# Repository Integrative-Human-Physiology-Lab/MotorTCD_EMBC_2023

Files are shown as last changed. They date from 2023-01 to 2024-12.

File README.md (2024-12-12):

# MOTORTCD

The motorTCD project enables the Transcranial doppler probe to be moved with the help of terminal commands. It enables the correct positioning of probe once again even if the signal is lost due to movements or slight jerk.
The project runs on Arduino Uno.

# **GETTING STARTED**
**1. Order the Off-The-Shelf Components:**

  Order the components as listed in the [Bill of Material](https://github.com/Integrative-Human-Physiology-Lab/MotorTCD_EMBC_2023/blob/main/Documentation/BOM.xlsx) for the project.

**2. Print the 3D-printable files:**

Print the STL file as shown in the [Print_Files](https://github.com/Integrative-Human-Physiology-Lab/MotorTCD_EMBC_2023/tree/main/Print_Files).

**3. Start the Assembly:**
The [Assembly Guide](https://github.com/Integrative-Human-Physiology-Lab/MotorTCD_EMBC_2023/blob/main/Documentation/assembly%20guide.pdf) shows you step by step process to assemble and wire the entire project with pictures. The entire assembly process is break down into following steps:
1. Assembly of 3D-printed components
2. Assembly of power components
3. Assembly of motor components
4. Assembly of Arduino with terminal and joystick shield
5. Wiring of all components
6. Final check to ensure connection

This step requires you to have all the components as listed in the Bill of Materials for our project.

**4. Upload the code:**
Connect the Arduino Uno to your computer and upload the Arduino Code.

# **Positioning reference: **

Whenever a signal is locked in. It is always advised that the harness for the TCD probe be placed in the center of the clamp boundaries. Repeated Experimentation has shown that due to the weight of the system, when the subject (individual being experimented on) is made to move in any direction, the TCD probe might be displaced by a very amount in the direction opposite to the moving direction of the subject. As this change in position is very miniscule, putting the probe in the center allows for the position to be adjusted in any direction. 

It is also advised that the person who operates the joystick familiarize themselves with the speed and movement of the clamp for better and more efficient reading.

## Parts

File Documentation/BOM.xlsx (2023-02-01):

Part | Mfct No. | Mfct. | Vendor Part No. | Vendor | Qty. | Unit Price (AUD) | Total | Description | Link
Motor drive controller | L9110S | ??? |  | Makestore.com.au (https://www.makerstore.com.au/product/elec-l9110s-d/) | 2 | $3.20 | $6.40 | DC Motor Drive Module Stepper Motor Drive Controller Board 2.5-12V H-Bridge Can Drive Dual DC Motor at The Same time or 4 Wire 2 Phase Stepper Motor
PLA Roll (White) | Ultimaker PLA | Ultimaker |  | imaginables.com.au (https://imaginables.com.au/collections/filaments/products/ultimaker-pla) | 1 | $76.90 | $76.90 | Ultimaker Material PLA Material White 2.85 mm
Motor | ??? | ??? |  | eBay (https://www.ebay.com/itm/Mini-5mm-2-phase-4-wire-3V-5V-Planetary-Gear-Stepper-Motor-linear-Screw-Slider/191911051181) | 2 | $5.62 | $11.24 | eBay Mini 5mm 2-phase 4-wire 3V 5V Planetary Gear Stepper Motor linear Screw Slider
Arduino Uno R3 | A000066 | ARDUINO CC | A000066 | core-electronics.com.au (https://core-electronics.com.au/arduino-uno-r3.html) | 1 | $35.85 | $35.85 | Controls the Motors
26 AWG, For soldering , Red | 1430-26-1-0500-004-1-TS | CNC Tech | CN472R-25-ND | Digikey (https://www.digikey.com.au/en/products/detail/cnc-tech/1430-26-1-0500-004-1-TS/7063370) | 1 | $11.54 | $11.54 | UL Style 1430 (to solder on motor pads), 26AWG, 4 lead Color Code 1 | Link (https://www.linengineering.com/resources/wiring-diagrams)
26 AWG, For soldering , Green | 1430-26-1-0500-007-1-TS | CNC Tech | CN475G-25-ND | Digikey (https://www.digikey.com.au/en/products/detail/cnc-tech/1430-26-1-0500-007-1-TS/7063373) | 1 | $11.54 | $11.54 | UL Style 1430 (to solder on motor pads), 26AWG, 4 lead Color Code 1 | Link (https://www.linengineering.com/resources/wiring-diagrams)
26 AWG, For soldering, Blue | 1430-26-1-0500-005-1-TS | CNC Tech | CN473L-25-ND | Digikey (https://www.digikey.com.au/en/products/detail/cnc-tech/1430-26-1-0500-005-1-TS/7063371) | 1 | $11.54 | $11.54 | UL Style 1430 (to solder on motor pads), 26AWG, 4 lead Color Code 1 | Link (https://www.linengineering.com/resources/wiring-diagrams)
26 AWG, For soldering, Black | 1430-26-1-0500-001-1-TS | CNC Tech | CN469B-25-ND | Digikey (https://www.digikey.com.au/en/products/detail/cnc-tech/1430-26-1-0500-001-1-TS/7063367) | 1 | $11.54 | $11.54 | UL Style 1430 (to solder on motor pads), 26AWG, 4 lead Color Code 1 | Link (https://www.linengineering.com/resources/wiring-diagrams)
3.3V regulator | AP3429A | Adafruit | ADA4711 | core-electronics.com.au (https://core-electronics.com.au/ap3429a-3-3v-buck-converter-breakout-3-3v-output-1-2a-max.html) | 1 | $7.60 | $7.60 | 3.3V Output 1.2A Max(Buck converter for stable 3V input to the motor)
Switchmode Plugpack(AC to DC Power) | MP-3316 | Core Electronics | CE04425 | core-electronics.com.au (https://core-electronics.com.au/27w-3-12vdc-switchmode-plugpack-with-usb-outlet.html) | 1 | $38.15 | $38.15 | 3V-12VDC 27W power supply(7 output plugs with USB outlet)
Arduino Terminal Block Shield |  | Freetronics | CE04491 | core-electronics.com.au (https://core-electronics.com.au/freetronics-terminal-shield-for-arduino.html) | 1 | $11.95 | $11.95 | Arduino 1.0 / "R3" layout breaks out all 30 pins on current-generation Arduino boards to screw terminals.
Screw kit 1.2-1.6mm |  | HTA | 15875 | hobbytools.com.au (https://www.hobbytools.com.au/Micro-Metric-Screws-600pc) | 1 | $16.48 | $16.48 | M1.6 x 4.5
Sand Paper set |  | Rocket | 1161524 | bunnings.com.au (https://www.bunnings.com.au/rocket-bulk-sanding-sheets-12-piece_p0335354?region_id=117364&gclsrc=aw.ds) | 1 | $8.90 | $8.90 | for roughing out edges during assembly of 3D printed parts
Insert |  |  | INSERTS-420 | serveronthemove.com.au (https://www.serveronthemove.com.au/products/420pc-set-of-knurled-threaded-inserts-m2-m3-m4-and-m5) | 1 | $28.88 | $28.88 | 420pc Set Of Knurled Threaded Inserts (M2, M3, M4 And M5)
Jumper wires for arduino(male,female, both) | ‎EL-CP-004 | ELEGOO |  | amazon.com.au (https://www.amazon.com.au/120pcs-Multicoloured-Dupont-Breadboard-arduino/dp/B01EV70C78?hvadid=341743944651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) | 1 | $9.96 | $9.96 | 120pcs Multicolored Dupont Wire 40pin Male to Female, 40pin Male to Male, 40pin Female to Female Breadboard Jumper Wires
Electrical Tape |  | Viaky | B0744B5DZ2 | amazon.com.au (https://www.amazon.com.au/Electrical-Insulation-Assorted-Colors-Industrial/dp/B0744B5DZ2?s=home-improvement) | 1 | $13.86 | $13.86 | Electrical Insulation Tape
2.1MM DC SOCKET WITH TERMINAL BLOCK | CGTime-00013 | zdyCGTime | B07LFRDSB7 | amazon.com.au (https://www.amazon.com/CGTime-Adapter-terminals-Connector-Security/dp/B07LFRDSB7) | 1 | $10.53 | $10.53 | 5.5 X 2.1mm Female Plug to 2 pin Female Screw terminals adapter

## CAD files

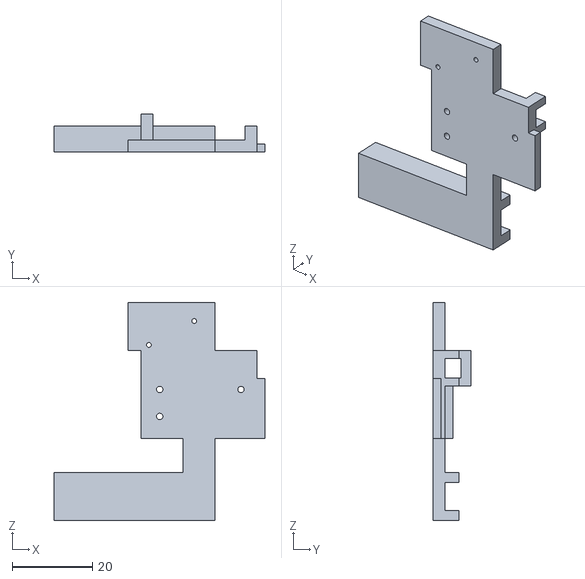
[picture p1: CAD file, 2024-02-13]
Print_Files/Motor Rack B 10_2.STL
52.7 x 9.50 x 54.5

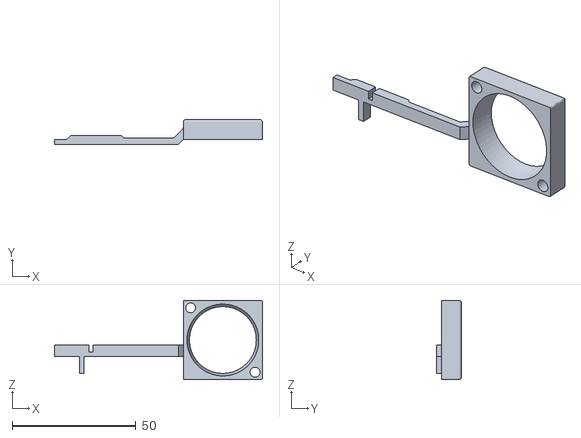
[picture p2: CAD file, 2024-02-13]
Print_Files/Prototype_10_Faceplate 9.STL
84.0 x 10.0 x 32.0

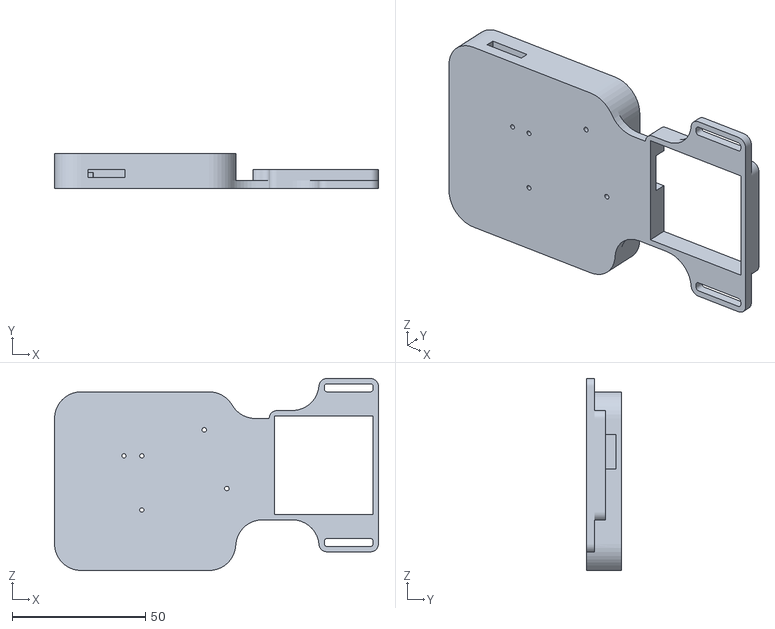
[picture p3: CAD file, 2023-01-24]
Print_Files/Motor Rack A 9.STL
121.5 x 13.0 x 72.0

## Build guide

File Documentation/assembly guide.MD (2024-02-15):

# Motor TCD Assembly Manual

## 1.  3D Printed Components Assembly

1. 	Remove all supports and raft from the print, it is important to ensure that all parts are free from excessive material especially the friction surfaces to ensure smooth movement of the device.

2. 	The motor racks consists of 2 parts - a hollow square at the front to attach to the strap and move the probe around a rectangular box to hold the motor.

3. There are 4 open holes on the rectangular box of motor rack: 1 at the back and 1 on the side for motor wires, 2 at the front to connect the faceplate and innerplate. 

4. With thin bar facing upwards, slide the headplate into through the upper hole on the front face of motor rack

5. Push the headplate as far back into the motor rack as possible 

6.  Tilt the faceplate at an angle where the thin bar is elevated as further away from the surface of motor rack as possible 

7. Align the hollow square of the motor plate with the thin bar of faceplate

8. Slide the inner plate underneath the thin bar at and angle, ensuring that the bar is still align with the hollow square, then, pushes the end of the bar into the square  
*Note: it is important that the small arm of the bar is located in between the closed hollow square and open hollow square)
  (An easier technique is to place the motor plate perpendicular to the end of the thin bar, let the thin bar touches the upper surface then rotate the motor plate slowly underneath the thin bar allowing the end of the bar to go through the hollow square)

9. After the open end of the bar has gone through the closed hollow square, push the 
inner plate forward the front face while also applying downward pressure so the motor 
plate lays flat onto the motor rack 

10. A 'click' sound should be hear when the motor plate snaps into place 

11. Ensure that all the movement are smooth (up and down movement along the motor plate of the faceplate and side movement of motor plate inside the motor rack)

12. If the movement is not smooth, remove the parts and smoothen all friction surface 
then repeat from step 4 

13. If all movements are smooth, close the lid of motor rack to complete the assembly 
(move rotation may be needed to put the lid into place)

## 2. Power Components Assembly

-Parts Needed: 
1. SwitchMode Plugpack(1) 
2. 2.1MM DC SOCKET WITH TERMINAL BLOCK (1) 
3. 22 AWG Wires: red and green (1 each 20 cm) 

- **Assembly Steps:** 

1. Turn the power output to 4.5V as the buck converter needs more than 3V for power source.

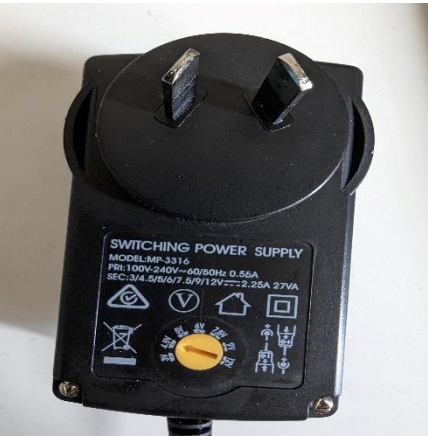
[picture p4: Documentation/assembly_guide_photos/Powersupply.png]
Power supply


2. Take 5.5*2.1 mm jack and plug at the end with matching the arrows. 

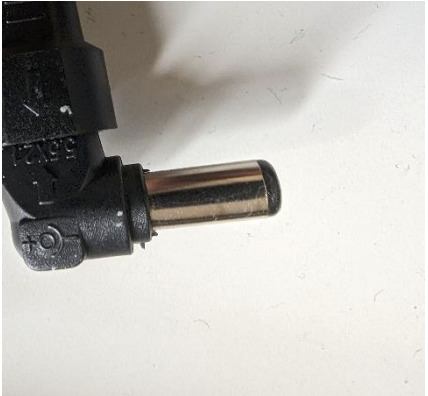
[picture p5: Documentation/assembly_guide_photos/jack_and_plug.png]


3. Wire the 2.1mm DC socket with Terminal Block. Strip the wires. Wire red wire to positive side and green wire to the ground.

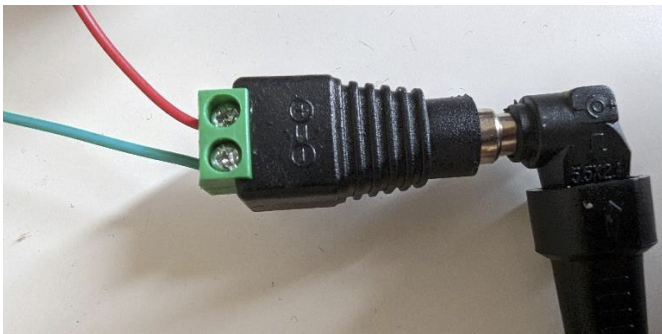
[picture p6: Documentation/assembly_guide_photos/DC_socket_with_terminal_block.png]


## 3. Motor Components Assembly

### a. Stepper Motor Soldering

- **Materials:** 

1. eBay Mini 5mm 2-phase 4-wire 3V 5V Planetary Gear Stepper Motor linear Screw 
Slider-(2 units) 
2. 26 AWG wire for soldering (Yellow, White, Black, Green)- 260 cm length for every 
wire-(2 units)

- **Procedure:**

1. Place the motor horizontally on table and stick the end of the motor flat onto the 
surface where soldering is to be done. 
2. Strip the wires into the length half of the size of the motor soldering plate. 
3. Now solder the wires into this order shown below: 

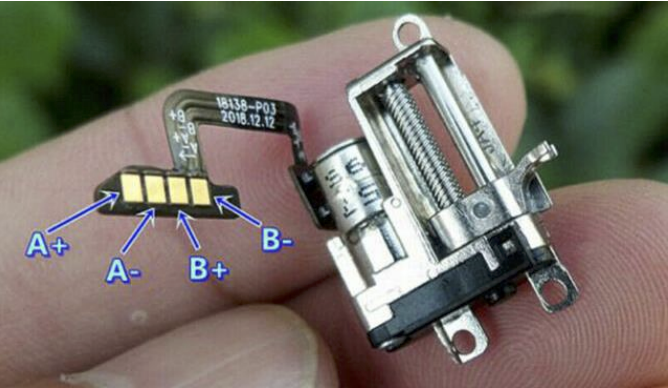
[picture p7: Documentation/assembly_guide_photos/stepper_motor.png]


A+ to yellow wire 

A - to white wire 

B+ to black wire 

B- to green wire

4. The soldering should be done carefully as the pad of motor is very small and two ends can join up during soldering. 
5. The final soldering of the motor look like this: 

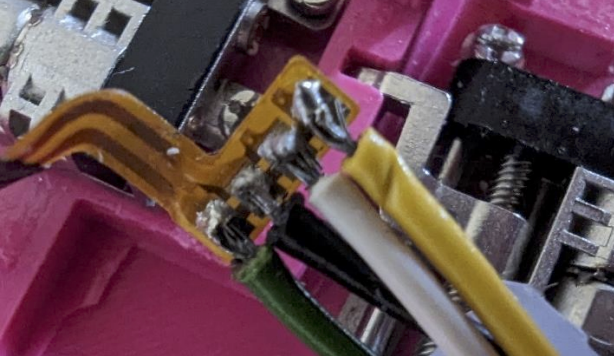
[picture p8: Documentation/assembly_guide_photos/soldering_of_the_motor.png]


6. Similarly, solder the second motor with similar wires in similar order. 

### b. Assembling Motor into 3D Printed Faceplate

- **Materials:** 
1. Soldered two stepper motors 
2. 3D printed Assembly 
3. M1.6*4.5 threaded bolts or screws 

- **Steps:** 
1. Of the two motors, one is responsible for vertical movements and one is 
responsible for horizontal movements. 
2. The vertical movement motor is fixed upon upper three 
holes as shown in figure with its linear actuator fixed in 
the opening to its side. Take three screws and screw the 
three hinges of motor as in figure. 

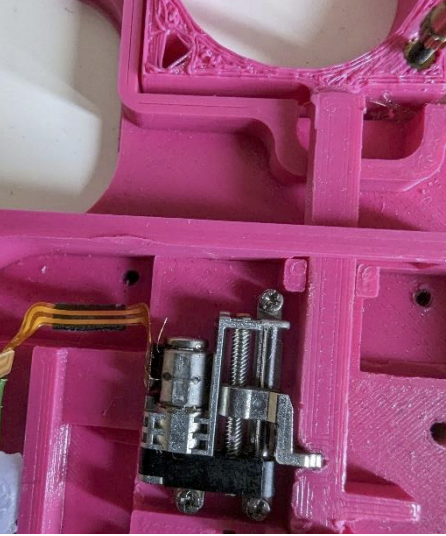
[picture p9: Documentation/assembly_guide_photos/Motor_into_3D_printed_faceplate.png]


3. Similarly, the horizontal movement motor is fixed in 
there holes below the motor with its actuator fixed in 
the opening. 

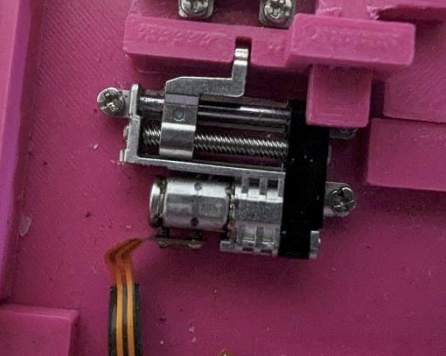
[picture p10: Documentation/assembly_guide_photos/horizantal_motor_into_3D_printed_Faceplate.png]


4. Now take the other end of the wires and line them up in their appropriate way and 
glue them in. There are two holes provided for the end of wires to follow along. 
The final sub-assembly look like this: 

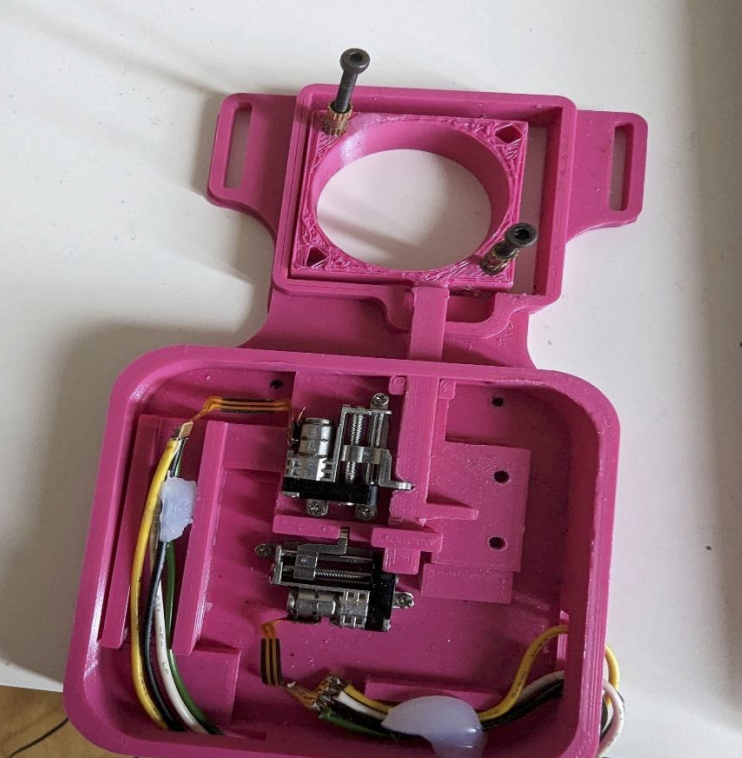
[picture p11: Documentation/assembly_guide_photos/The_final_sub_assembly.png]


### c. Soldering and Wiring 3V Regulator

- **Materials:** 
1. 3V Buck converter set 
2. Some Arduino jumper wires female-female (orange, red and green) 

Steps: 
1. Take the buck converter set and solder the pins into place like 
this. 

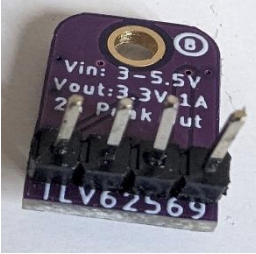
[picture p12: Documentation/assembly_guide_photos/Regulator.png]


2. Now, cut the jumper wires into half and strip the end. 

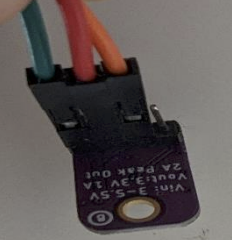
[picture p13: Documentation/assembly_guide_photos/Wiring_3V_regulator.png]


3. Now there are three pins which should be connected to jumper 
wires female like listed below: 
Vin-orange    GND-green   3V-red 

### d. Connecting Stepper Motor Drive Controller

Parts needed: 
1. Sub-assembly obtained from step b 
2. Stepper Motor Drive Controller *2 
3. Arduino female-female jumper wires (2*green, 1*yellow, 1*white, 1*black, 
1*red) *2

Steps: 
1. Strip the loose ends of wire coming from two stepper motor. 
2. Now, these wires (4 each) is connected to the stepper motor drive controller. 
3. Take all 4 wires (yellow, white, black green) from a motor with vertical 
movements and a motor drive controller green end.  
4. The yellow and white wire is wired into Motor A and 
black and green is wired into Motor B. Take reference 
of the picture: 

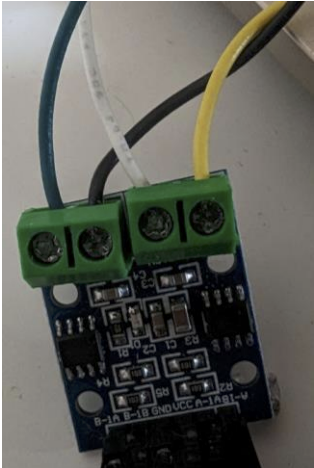
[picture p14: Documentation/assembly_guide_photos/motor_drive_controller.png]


5. Similarly, wire the other motor controller drive with the 
horizontal movement motor. 

6. Now, the opposite end of motor drive controller has 
pins where female Arduino jumper wires should be 
connected. 

7. Cut the Arduino jumper wires into the half and strip the end. 

8. Now connect the female end of jumper wire to the corresponding pin as listed 
below: 

A-1B with yellow 

A-1A with white 

VCC with red 

GND with green 

B-1B with black 

B-1A with green 

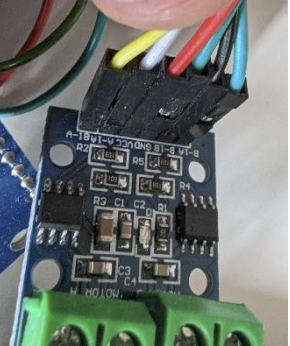
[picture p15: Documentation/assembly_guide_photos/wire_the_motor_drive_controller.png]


9. Similarly, follow the similar steps for another motor and this section is complete. 

## 4. Arduino with Terminal and Joystick Shield Assembly

- **Components:** 
1. Arduino Uno * 1 
2. Terminal Shield *1 
3. Joystick Shield Funduino *1 

Steps: 
1. Take Arduino Uno and on top of that place the terminal shield by aligning the digital and 
analog pins of Arduino with that of terminal shield. 
2. Now take joystick shield and place on top of the black female pins of terminal shield. 
Align the shield accordingly with the number of pins per side. 
3. The sub-assembly is complete. 

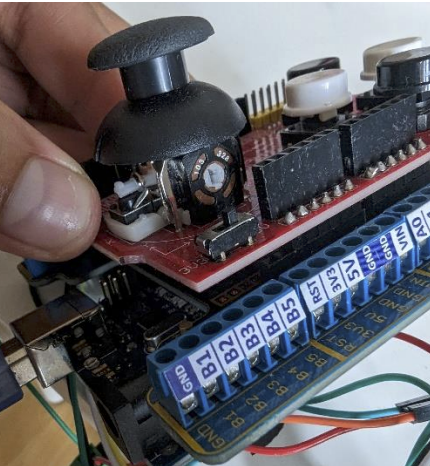
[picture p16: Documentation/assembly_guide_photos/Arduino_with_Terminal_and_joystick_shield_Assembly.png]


## 5. Final Wiring and Check

Parts Needed: 
1. All sub-assemblies created till now. 
2. Green 26 AWG wire of length 20 cm. 

Steps: 
1. Power terminal sub assembly with 3V regulator and Arduino: 
The end of the 2.1MM DC SOCKET WITH TERMINAL BLOCK has two green and 
red loose wires. Strip the end of these wires if needed. Screw the green wire into near 
ground terminal (GND) in Terminal shield. Connect the red wire to the orange wire of 
the 3V regulator. 

2. 3V regulator with motor drive controllers and Arduino. 
Take red wires of the two-motor drive controller (one each) and connect with the red 
wire of 3V regulator. These three wires must be joined together and bonded by an 
electrical tape. 
Now take Green 26 AWG wire of length 20 cm and strip both ends. Take green wires 
(GND not B-1A) of the two motor drive controller (one each) and connect with the 
green wire of 3V regulator and the one end of the Green 26 AWG wire of length 20 
cm. These four wires must be joined together and bonded by an electrical tape. Now 
take the free end of Green 26 AWG wire of length 20 cm and connect to the near 
ground terminal (GND) in Terminal shield. 

3. Motor drive controller with Arduino 
Now there are four wires (yellow, white, black and green) left in motor drive controller 
which should be connected to the respective pins in Arduino.  

|Vertical Movement Motor | Horizontal Movement Motor| 
|----------- | ----------- |
| Yellow(A2) | Yellow(D9) |
| White(A3) | White(D10) |
|Black(A4)  | Black(D11) |
|Green(A5)  |Green(D12) |
 
Connect these wires into Terminal shield and screw it accordingly. 

5. Final Check 

• Connect the power supply and both red LED from motor controller drivers should 
turn on. If not, check your connect again from Step 2 and check the wiring as grounds should be connected properly

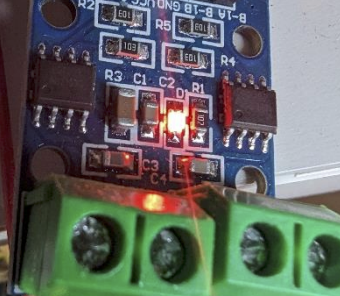
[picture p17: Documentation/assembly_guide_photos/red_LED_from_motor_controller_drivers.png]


• Upload code into the Arduino and try to run with joysticks. If there is no red LED in joystick shield, check your connection in Step 3. If any problems by running the 
joystick, see the correct wires are connected to correct pins in terminal shield. 

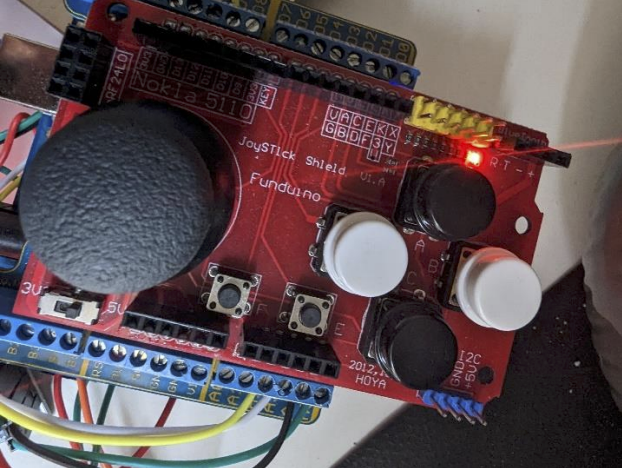
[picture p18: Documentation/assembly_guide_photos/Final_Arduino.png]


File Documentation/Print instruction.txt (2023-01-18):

3D print instruction

Our Motor TCD prototype was printed unsing Utlimaker S5.
Hence, the following settings are the settings that we use in Ultimaker Cura
slicer version 5.1.1

Print material: 
- Primary (to use for printing of part): Ultimaker PLA Magenta, print core AA 0.4
- Secondary (to use for printing the support and raft):  
Resoluion: 0.1mm
infill: 20%
Support: on (printed with dissovable material)
Adhesion: on

Total number of layers: 129
Total material used: 53g - 6.72 m
Time for the print to complete: 11 hours 54 minutes

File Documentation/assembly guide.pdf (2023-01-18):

MOTOR TCD

ASSEMBLY MANUAL

## 1. 3d printed Components Assembly

1. Remove all supports and raft from the print, it is important to ensure that all parts are free from excessive material especially the friction surfaces to ensure smooth movement of the device.
2. The motor racks consists of 2 components, a hollow square at the front to attach to the strap and move the probe around a rectangular box to hold the motor
3. There are 4 open holes on the rectangular box of motor rack: 1 at the back and 1 on the side for motor wires, 2 at the front to connect the faceplate and innerplate.
4. With thin bar facing upwards, slide the headplate into through the upper hole on the front face of motor rack
5. Push the headplate as far back into the motor rack as possible
6. Tilt the faceplate at an angle where the thin bar is elevated as further away from the surface of motor rack as possible
7. Align the hollow square of the motor plate with the thin bar of faceplate
8. Slide the inner plate underneath the thin bar at and angle, ensuring that the bar is still align with the hollow square, then, pushes the end of the bar into the square
*Note: it is important that the small arm of the bar is located in between the closed hollow square and open hollow square)
(An easier technique is to place the motor plate perpendicular to the end of the thin bar, let the thin bar touches the upper surface then rotate the motor plate slowly underneath the thin bar allowing the end of the bar to go through the hollow square.)
9. After the open end of the bar has gone through the closed hollow square, push the inner plate forward the front face while also applying downward pressure so the motor plate lays flat onto the motor rack
10. A 'click' sound should be hear when the motor plate snaps into place
11. Ensure that all the movement are smooth (up and down movement along the motor plate of the faceplate and side movement of motor plate inside the motor rack)

12. If the movement is not smooth, remove the parts and smoothen all friction surface then repeat from step 4
13. If all movements are smooth, close the lid of motor rack to complete the assembly (move rotation may be needed to put the lid into place)

## 2. Power Components Assembly

Parts Needed:
1. SwitchMode Plugpack(1)
2. 2.1MM DC SOCKET WITH TERMINAL BLOCK (1)
3. 22 AWG Wires: red and green (1 each 20 cm)

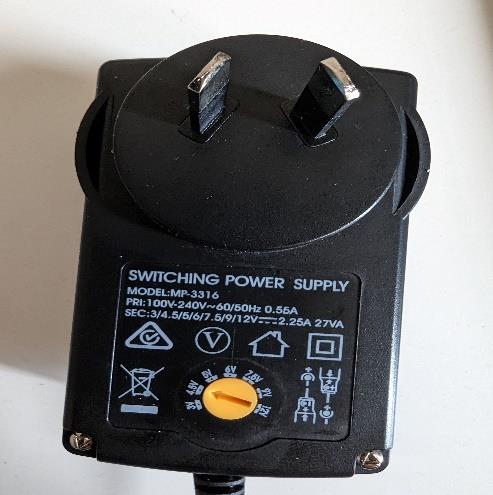
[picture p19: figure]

ASSEMBLY STEPS:

1. Turn the power output to 4.5V as the buck converter needs more than 3V for power source.
2. Take 5.5*2.1 mm jack and plug at the end with matching the arrows.
3. Wire the 2.1mm DC socket with Terminal Block.

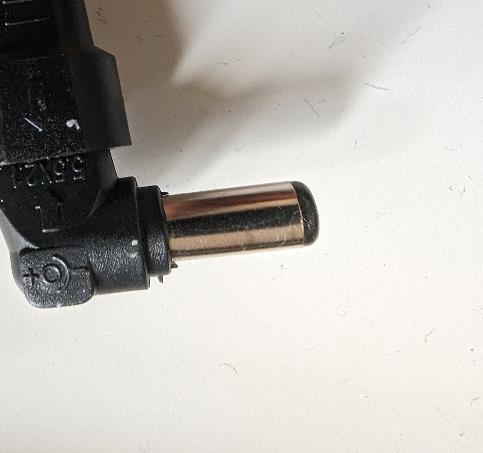
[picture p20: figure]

Strip the wires. Wire red wire to positive side and green wire to the ground.

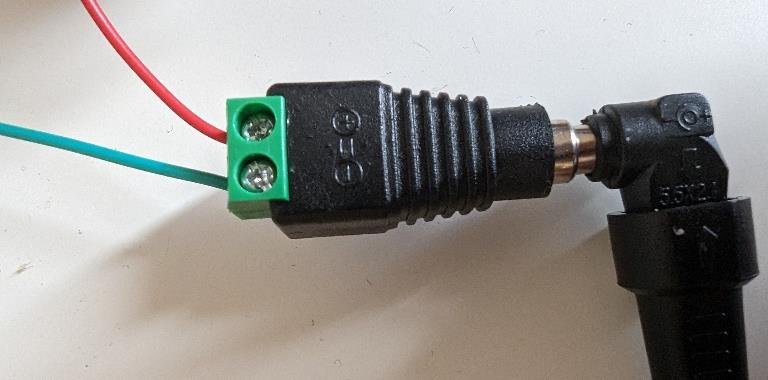
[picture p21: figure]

## 3. Motor Components Assembly:

a. Soldering of stepper motor
Parts Needed:
1. eBay Mini 5mm 2-phase 4-wire 3V 5V Planetary Gear Stepper Motor linear Screw Slider-(2 units)
2. 26 AWG wire for soldering (Yellow, White, Black, Green)- 260 cm length for every wire-(2 units)

Steps:

1. Place the motor horizontally on table and stick the end of the motor flat onto the surface where soldering is to be done.
2. Strip the wires into the length half of the size of the motor soldering plate.
3. Now solder the wires into this order shown below:

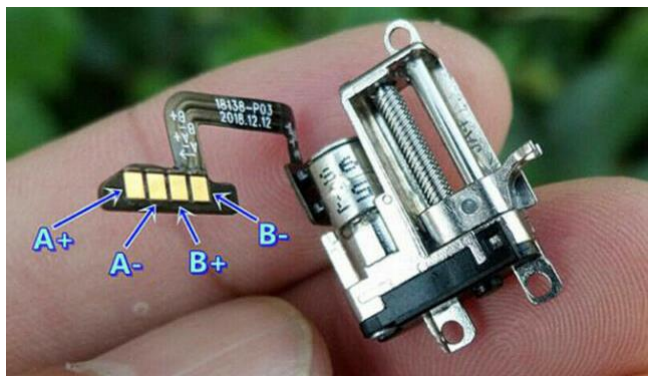
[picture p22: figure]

A+ to yellow wire

A - to white wire

B+ to black wire

B- to green wire

4. The soldering should be done carefully as the pad of motor is very small and two ends can join up during soldering.
5. The final soldering of the motor look like this:

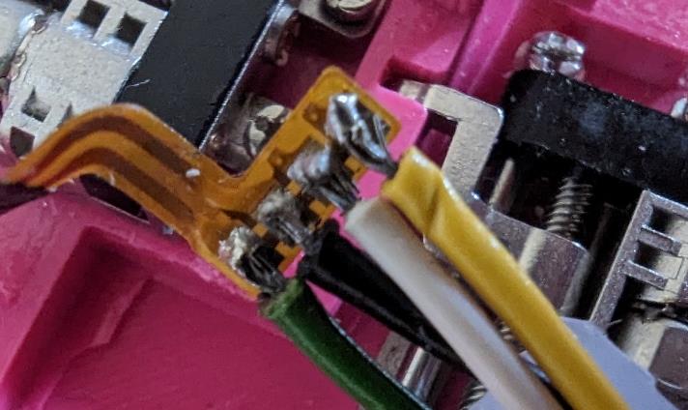
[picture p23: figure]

6. Similarly, solder the second motor with similar wires in similar order.
b. Assembling the motor into 3D printed Faceplate
Parts needed:
1. Soldered two stepper motors
2. 3D printed Assembly
3. M1.6*4.5 threaded bolts or screws

Steps:

1. Of the two motors, one is responsible for vertical movements and one is responsible for horizontal movements.
2. The vertical movement motor is fixed upon upper three
holes as shown in figure with its linear actuator fixed in
the opening to its side. Take three screws and screw the three hinges of motor as in figure.

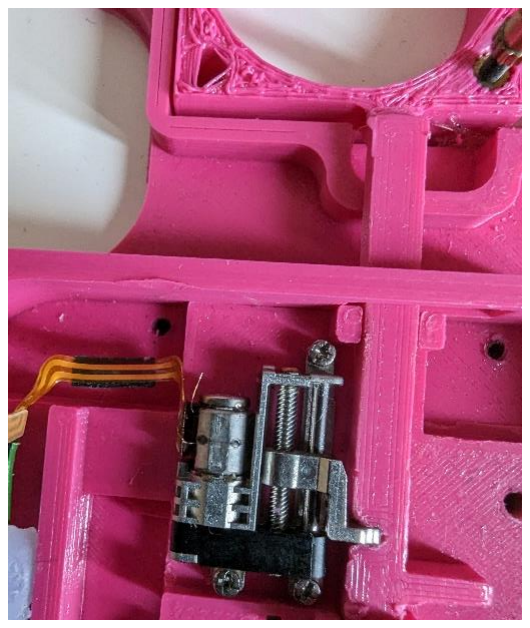
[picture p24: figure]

3. Similarly, the horizontal movement motor is fixed in there holes below the motor with its actuator fixed in the opening.

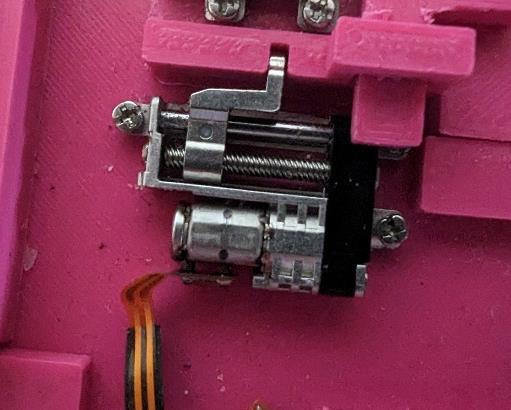
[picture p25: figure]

4. Now take the other end of the wires and line them up in their appropriate way and glue them in. There are two holes provided for the end of wires to follow along. The final sub-assembly look like this:

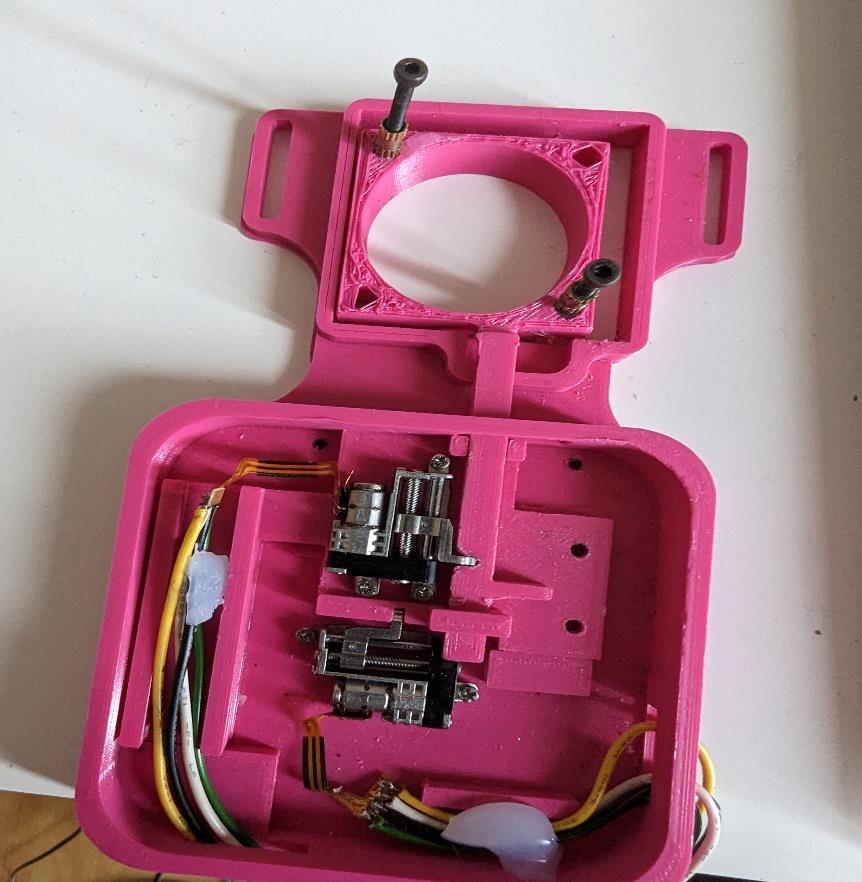
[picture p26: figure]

c. Soldering and Wiring 3V regulator
Parts needed:
1. 3V Buck converter set
2. Some Arduino jumper wires female-female (orange, red and green)

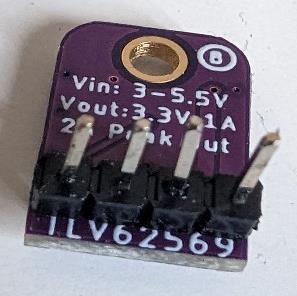
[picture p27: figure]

Steps:

1. Take the buck converter set and solder the pins into place like this.
2. Now, cut the jumper wires into half and strip the end.

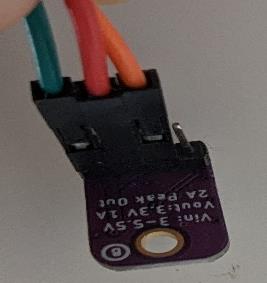
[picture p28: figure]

3. Now there are three pins which should be connected to jumper wires female like listed below:
Vin-orange GND-green 3V-red
d. Connecting the stepper motor drive controller Parts needed:
1. Sub-assembly obtained from step b
2. Stepper Motor Drive Controller *2
3. Arduino female-female jumper wires (2*green, 1*yellow, 1*white, 1*black, 1*red) *2

Steps:

1. Strip the loose ends of wire coming from two stepper motor.
2. Now, these wires (4 each) is connected to the stepper motor drive controller.
3. Take all 4 wires (yellow, white, black green) from a motor with vertical movements and a motor drive controller green end.
4. The yellow and white wire is wired into Motor A and
black and green is wired into Motor B. Take reference
of the picture:
5. Similarly, wire the other motor controller drive with the horizontal movement motor.
6. Now, the opposite end of motor drive controller has pins where female Arduino jumper wires should be connected.

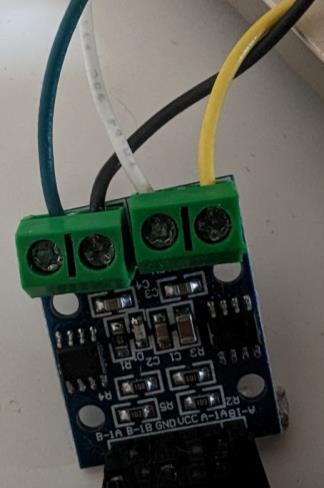
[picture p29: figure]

7. Cut the Arduino jumper wires into the half and strip the end.

8. Now connect the female end of jumper wire to the corresponding pin as listed below:
A-1B with yellow
A-1A with white
VCC with red
GND with green
B-1B with black
B-1A with green

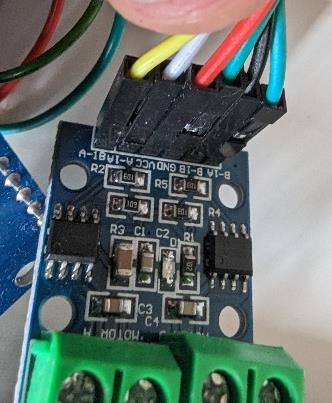
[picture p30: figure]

9. Similarly, follow the similar steps for another motor and this section is complete.

## 3. Arduino with Terminal and joystick shield Assembly

Parts Needed:

1. Arduino Uno * 1
2. Terminal Shield *1
3. Joystick Shield Funduino *1

Steps:

1. Take Arduino Uno and on top of that place the terminal shield by aligning the digital and analog pins of Arduino with that of terminal shield.
2. Now take joystick shield and place on top of the black female pins of terminal shield. Align the shield accordingly with the number of pins per side.
3. The sub-assembly is complete.

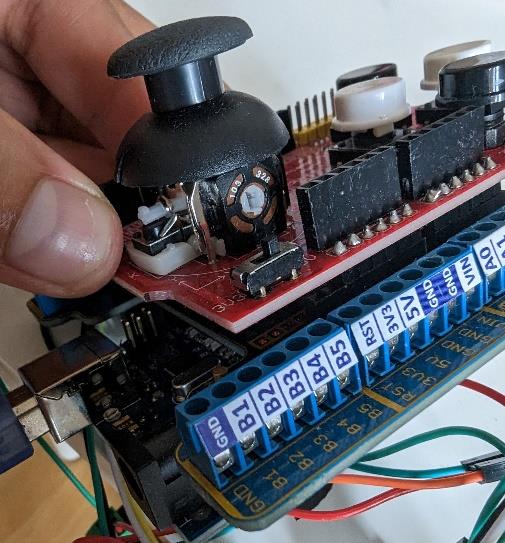
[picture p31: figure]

## 4. Final wiring

Parts Needed:
1. All sub-assemblies created till now.
2. Green 26 AWG wire of length 20 cm.

Steps:

### 1. Power terminal sub assembly with 3V regulator and Arduino:

The end of the 2.1MM DC SOCKET WITH TERMINAL BLOCK has two green and red loose wires. Strip the end of these wires if needed. Screw the green wire into near ground terminal (GND) in Terminal shield. Connect the red wire to the orange wire of the 3V regulator.

2. 3V regulator with motor drive controllers and Arduino.
Take red wires of the two-motor drive controller (one each) and connect with the red wire of 3V regulator. These three wires must be joined together and bonded by an electrical tape.
Now take Green 26 AWG wire of length 20 cm and strip both ends. Take green wires (GND not B-1A) of the two motor drive controller (one each) and connect with the green wire of 3V regulator and the one end of the Green 26 AWG wire of length 20 cm. These four wires must be joined together and bonded by an electrical tape. Now take the free end of Green 26 AWG wire of length 20 cm and connect to the near ground terminal (GND) in Terminal shield.

### 3. Motor drive controller with Arduino

Now there are four wires (yellow, white, black and green) left in motor drive controller which should be connected to the respective pins in Arduino.
Vertical Movement Motor | Horizontal Movement Motor
Yellow(A2) | Yellow(D9)
White(A3) | White(D10)
Black(A4) | Black(D11)
Green(A5) | Green(D12)

Connect these wires into Terminal shield and screw it accordingly.

## 5. Final Check

- Connect the power supply and both red LED from motor controller drivers should turn on. If not, check your connect again from Step 2 and check the wiring as grounds should be connected properly.

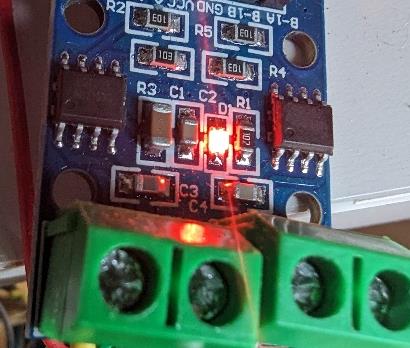
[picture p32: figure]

- Upload code into the Arduino and try to run with joysticks. If there is no red LED in joystick shield, check your connection in Step 3. If any problems by running the joystick, see the correct wires are connected to correct pins in terminal shield.

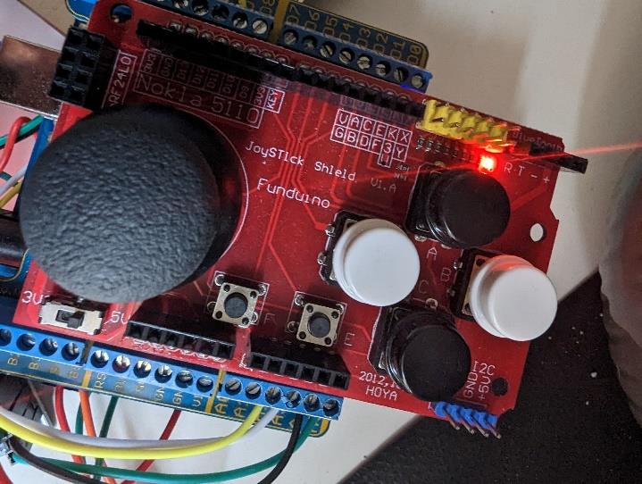
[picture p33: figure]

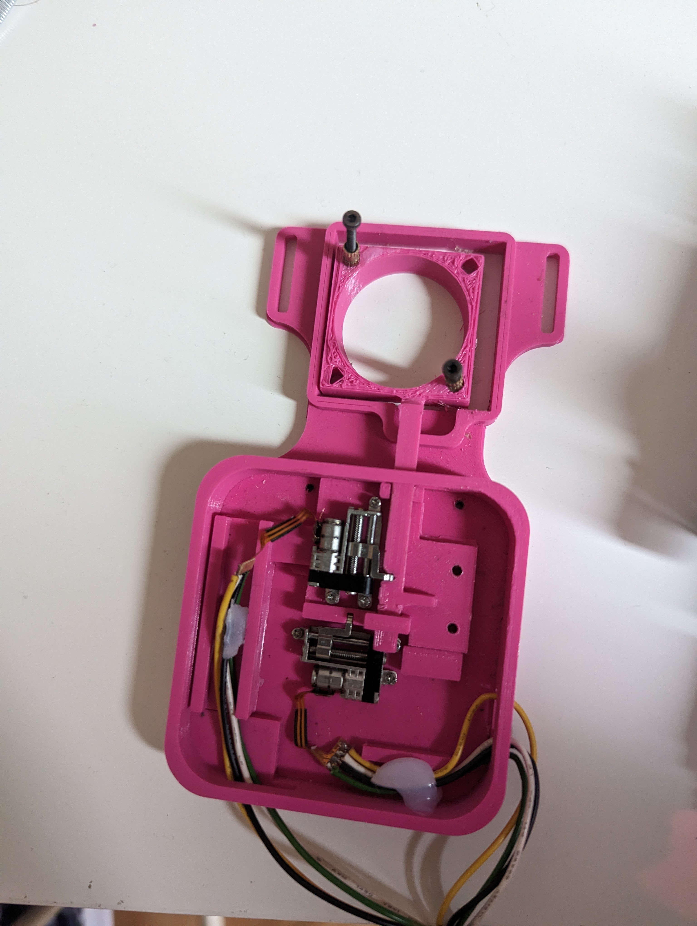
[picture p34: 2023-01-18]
Photo/3d print with motor.jpg

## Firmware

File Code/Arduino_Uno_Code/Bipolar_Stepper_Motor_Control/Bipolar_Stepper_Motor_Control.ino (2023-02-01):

/*
   Credits to Robin2 for his serial parsing tutorial, from which parts of
   this code regarding serial inputs are heavily derived from:
   https://forum.arduino.cc/t/serial-input-basics-updated/382007
*/

/*
   Motor cable order
   A_bar / A / B_bar / B
   Black / Red / Yellow / Green
*/

// for our up/down motor
#define A1_bar    2                  // the pin connected to the wire A- of the coil A (or to the H-bridge pin controlling the same wire) 
#define A1        3                  // the pin connected to the wire A of the coil A (or to the H-bridge pin controlling the same wire)
#define B1_bar    4                  // the pin connected to the wire B- of the coil B (or to the H-bridge pin controlling the same wire)
#define B1        5                  // the pin connected to the wire B of the coil B (or to the H-bridge pin controlling the same wire)
// for our left/right motor
#define A2_bar    8                  // the pin connected to the wire A- of the coil A (or to the H-bridge pin controlling the same wire) 
#define A2        9                  // the pin connected to the wire A of the coil A (or to the H-bridge pin controlling the same wire)
#define B2_bar    10                 // the pin connected to the wire B- of the coil B (or to the H-bridge pin controlling the same wire)
#define B2        11                 // the pin connected to the wire B of the coil B (or to the H-bridge pin controlling the same wire)
// motor control variables
#define x        1000                // smaller values may make the motor produce more speed and less torque
// Note: approximate distance is 6.2um/step for current motors

/*
   Serial Parsing instantiations
   includes variables for storing data, holding parsed data, and new data input checks
*/

const byte numChars = 32;
char receivedChars[numChars];
char tempChars[numChars];            // temporary array for use when parsing

char stepDirection[numChars] = {0};
int steps = 0;

boolean newData = false;

/*
   Limit switch pin/interrupt instantiations
   Note: these pins vary depending on the board used. Validate at
   https://www.arduino.cc/reference/en/language/functions/external-interrupts/attachinterrupt/
*/
byte up = 18;
byte down = 19;
byte left = 20;
byte right = 21;

bool upTrigger = 0;
bool downTrigger = 0;
bool leftTrigger = 0;
bool rightTrigger = 0;

//======== For limit switch interrupts ==========//
void limitUp() {
  if (digitalRead(up) == HIGH) {
    upTrigger = 0;
    digitalWrite(LED_BUILTIN, LOW);
  } else {
    upTrigger = 1;
    digitalWrite(LED_BUILTIN, HIGH);
  }
}

void limitDown() {
  if (digitalRead(down) == HIGH) {
    downTrigger = 0;
    digitalWrite(LED_BUILTIN, LOW);
  } else {
    downTrigger = 1;
    digitalWrite(LED_BUILTIN, HIGH);
  }
}

void limitLeft() {
  if (digitalRead(left) == HIGH) {
    leftTrigger = 0;
    digitalWrite(LED_BUILTIN, LOW);
  } else {
    leftTrigger = 1;
    digitalWrite(LED_BUILTIN, HIGH);
  }
}

void limitRight() {
  if (digitalRead(right) == HIGH) {
    rightTrigger = 0;
    digitalWrite(LED_BUILTIN, LOW);
  } else {
    rightTrigger = 1;
    digitalWrite(LED_BUILTIN, HIGH);
  }
}

//========== For detecting start/end markers in Serial input ===========//
void recvWithStartEndMarkers() {
  static boolean recvInProgress = false;
  static byte ndx = 0;
  char startMarker = '<';
  char endMarker = '>';
  char rc;

  while (Serial.available() > 0 && newData == false) {
    rc = Serial.read();
    if (recvInProgress == true) {
      if (rc != endMarker) {
        receivedChars[ndx] = rc;
        ndx++;
        if (ndx >= numChars) {
          ndx = numChars - 1;
        }
      } else {
        receivedChars[ndx] = '\0'; // terminate the string
        recvInProgress = false;
        ndx = 0;
        newData = true;
      }
    } else if (rc == startMarker) {
      recvInProgress = true;
    }
  }
}

//=========== For parsing Serial input data ============//
void parseData() {      // split the data into its parts
  char * strtokIndx; // this is used by strtok() as an index
  strtokIndx = strtok(tempChars, ",");
  strcpy(stepDirection, strtokIndx);
  strtokIndx = strtok(NULL, ",");
  steps = atoi(strtokIndx);
}

//============= To show parsed Serial inputs ==============//
void showParsedData() {
  Serial.print("Direction ");
  Serial.println(stepDirection);
  Serial.print("Steps ");
  Serial.println(steps);
}



//============ for motor control ================//

void MotorsOn1() { // turns on motors, to start operating
  pinMode(A1, OUTPUT);
  pinMode(A1_bar, OUTPUT);
  pinMode(B1, OUTPUT);
  pinMode(B1_bar, OUTPUT);
}

void MotorsOff1() { // turns off motors, to stop current draw. Useful after moving, or when not operating
  pinMode(A1, INPUT);
  digitalWrite(A1, HIGH);
  pinMode(A1_bar, INPUT);
  digitalWrite(A1_bar, HIGH);
  pinMode(B1, INPUT);
  digitalWrite(B1, HIGH);
  pinMode(B1_bar, INPUT);
  digitalWrite(B1_bar, HIGH);
}

void MotorsOn2() { // turns on motors, to start operating
  pinMode(A2, OUTPUT);
  pinMode(A2_bar, OUTPUT);
  pinMode(B2, OUTPUT);
  pinMode(B2_bar, OUTPUT);
}

void MotorsOff2() { // turns off motors, to stop current draw. Useful after moving, or when not operating
  pinMode(A2, INPUT);
  digitalWrite(A2, HIGH);
  pinMode(A2_bar, INPUT);
  digitalWrite(A2_bar, HIGH);
  pinMode(B2, INPUT);
  digitalWrite(B2, HIGH);
  pinMode(B2_bar, INPUT);
  digitalWrite(B2_bar, HIGH);
}

void StepUp() {
  MotorsOn1();
  for (int i = 0; i < (steps / 4) ; i++) {
    if (upTrigger) {
      Serial.println("Upper limit switch detects collision");
      break;
    }
    digitalWrite(A1, HIGH);
    digitalWrite(A1_bar, LOW);
    digitalWrite(B1, HIGH);
    digitalWrite(B1_bar, LOW);
    delayMicroseconds (x);

    if (upTrigger) {
      Serial.println("Upper limit switch detects collision");
      break;
    }
    digitalWrite(A1, LOW);
    digitalWrite(A1_bar, HIGH);
    digitalWrite(B1, HIGH);
    digitalWrite(B1_bar, LOW);
    delayMicroseconds (x);

    if (upTrigger) {
      Serial.println("Upper limit switch detects collision");
      break;
    }
    digitalWrite(A1, LOW);
    digitalWrite(A1_bar, HIGH);
    digitalWrite(B1, LOW);
    digitalWrite(B1_bar, HIGH);
    delayMicroseconds (x);

    if (upTrigger) {
      Serial.println("Upper limit switch detects collision");
      break;
    }
    digitalWrite(A1, HIGH);
    digitalWrite(A1_bar, LOW);
    digitalWrite(B1, LOW);
    digitalWrite(B1_bar, HIGH);
    delayMicroseconds (x);
  }
  Serial.println("StepUp Subroutine Complete");
  MotorsOff1();
}

void StepDown() {
  MotorsOn1();
  for (int i = 0; i < (steps / 4); i++) {
    if (downTrigger) {
      Serial.println("Lower limit switch detects collision");
      break;
    }
    digitalWrite(A1, HIGH);
    digitalWrite(A1_bar, LOW);
    digitalWrite(B1, LOW);
    digitalWrite(B1_bar, HIGH);
    delayMicroseconds (x);

    if (downTrigger) {
      Serial.println("Lower limit switch detects collision");
      break;
    }
    digitalWrite(A1, LOW);
    digitalWrite(A1_bar, HIGH);
    digitalWrite(B1, LOW);
    digitalWrite(B1_bar, HIGH);
    delayMicroseconds (x);

    if (downTrigger) {
      Serial.println("Lower limit switch detects collision");
      break;
    }
    digitalWrite(A1, LOW);
    digitalWrite(A1_bar, HIGH);
    digitalWrite(B1, HIGH);
    digitalWrite(B1_bar, LOW);
    delayMicroseconds (x);

    if (downTrigger) {
      Serial.println("Lower limit switch detects collision");
      break;
    }
    digitalWrite(A1, HIGH);
    digitalWrite(A1_bar, LOW);
    digitalWrite(B1, HIGH);
    digitalWrite(B1_bar, LOW);
    delayMicroseconds (x);
  }
  Serial.println("StepDown Subroutine Complete");
  MotorsOff1();
}

void StepLeft() {
  MotorsOn2();
  for (int i = 0; i < (steps / 4) ; i++) {
    if (leftTrigger) {
      Serial.println("Left limit switch detects collision");
      break;
    }
    digitalWrite(A2, HIGH);
    digitalWrite(A2_bar, LOW);
    digitalWrite(B2, HIGH);
    digitalWrite(B2_bar, LOW);
    delayMicroseconds (x);

    if (leftTrigger) {
      Serial.println("Left limit switch detects collision");
      break;
    }
    digitalWrite(A2, LOW);
    digitalWrite(A2_bar, HIGH);
    digitalWrite(B2, HIGH);
    digitalWrite(B2_bar, LOW);
    delayMicroseconds (x);

    if (leftTrigger) {
      Serial.println("Left limit switch detects collision");
      break;
    }
    digitalWrite(A2, LOW);
    digitalWrite(A2_bar, HIGH);
    digitalWrite(B2, LOW);
    digitalWrite(B2_bar, HIGH);
    delayMicroseconds (x);

    if (leftTrigger) {
      Serial.println("Left limit switch detects collision");
      break;
    }
    digitalWrite(A2, HIGH);
    digitalWrite(A2_bar, LOW);
    digitalWrite(B2, LOW);
    digitalWrite(B2_bar, HIGH);
    delayMicroseconds (x);
  }
  Serial.println("StepLeft Subroutine Complete");
  MotorsOff2();
}

void StepRight() {
  MotorsOn2();
  for (int i = 0; i < (steps / 4); i++) {
    if (rightTrigger) {
      Serial.println("Right limit switch detects collision");
      break;
    }
    digitalWrite(A2, HIGH);
    digitalWrite(A2_bar, LOW);
    digitalWrite(B2, LOW);
    digitalWrite(B2_bar, HIGH);
    delayMicroseconds (x);

    if (rightTrigger) {
      Serial.println("Right limit switch detects collision");
      break;
    }
    digitalWrite(A2, LOW);
    digitalWrite(A2_bar, HIGH);
    digitalWrite(B2, LOW);
    digitalWrite(B2_bar, HIGH);
    delayMicroseconds (x);

    if (rightTrigger) {
      Serial.println("Right limit switch detects collision");
      break;
    }
    digitalWrite(A2, LOW);
    digitalWrite(A2_bar, HIGH);
    digitalWrite(B2, HIGH);
    digitalWrite(B2_bar, LOW);
    delayMicroseconds (x);

    if (rightTrigger) {
      Serial.println("Right limit switch detects collision");
      break;
    }
    digitalWrite(A2, HIGH);
    digitalWrite(A2_bar, LOW);
    digitalWrite(B2, HIGH);
    digitalWrite(B2_bar, LOW);
    delayMicroseconds (x);
  }
  Serial.println("StepRight Subroutine Complete");
  MotorsOff2();
}

//=================== Arduino Setup ===================//
void setup() {
  // setting our motor pin states as internal pull-up until ready to actuate
  MotorsOff1();
  MotorsOff2();

  // For Serial Monitor
  Serial.begin(9600);
  Serial.println("Enter commands in the form of <stepDirection,steps>");
  Serial.println("valid stepDirections are {up,down,left,right}");
  Serial.println();

  // For limit switch interrupts
  digitalWrite(up,    HIGH);
  digitalWrite(down,  HIGH);
  digitalWrite(left,  HIGH);
  digitalWrite(right, HIGH);

  // These require different syntax for arduino uno rev2 wifi, differ per board. Check:
  // https://www.arduino.cc/reference/en/language/functions/external-interrupts/attachinterrupt/
  attachInterrupt(digitalPinToInterrupt(up), limitUp,    CHANGE);
  attachInterrupt(digitalPinToInterrupt(down), limitDown,  CHANGE);
  attachInterrupt(digitalPinToInterrupt(left), limitLeft,  CHANGE);
  attachInterrupt(digitalPinToInterrupt(right), limitRight, CHANGE);

  // Built-in LED to flash when we hit any of our limit switches
  pinMode(LED_BUILTIN, OUTPUT);
}

//============= Main loop ================//
void loop() {
  // Scrape for data from Serial Monitor
  recvWithStartEndMarkers();
  // If new input, begin subroutine
  if (newData == true) {
    strcpy(tempChars, receivedChars);
    // this temporary copy is necessary to protect the original data
    //   because strtok() used in parseData() replaces the commas with \0
    parseData();
    showParsedData();
    newData = false; // ensures we don't have infinite loop

    // Comparing input to determine direction of operation (if any) and instigating operation
    if (strcmp(stepDirection, "up") == 0) {
      StepUp();
    }
    if (strcmp(stepDirection, "down") == 0) {
      StepDown();
    }
    if (strcmp(stepDirection, "left") == 0) {
      StepLeft();
    }
    if (strcmp(stepDirection, "right") == 0) {
      StepRight();
    }
  }
}

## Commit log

2023-01-18 Assembly guide update
2023-01-18 bill of materials update
    [BOM.xlsx]
2023-01-23 Added Arduino Joystick Code with Limit Switches
2023-01-24 print files added
    [Motor Rack A 9.STL, Motor Rack B 9 .STL]
2023-01-24 Updated BOM (not complete)
    [BOM.xlsx]
2023-01-25 BOM update
    [BOM.xlsx]
2023-02-01 Removing extraneous files. Added demo video
    [BOM.xlsx]
2023-02-01 Added Arduino Code to control motorTCD
2023-12-21 Fixed PrintFiles Link
2023-12-21 Fixed Assembly Guide Link
2024-02-13 Changed Faceplate
    Rounded off the edges on faceplate so it does not stab the participant.
    SolidWorks Design change:
    Noora Files Prototype 10
    [Faceplate .STL, Prototype_10_Faceplate 9.STL]
2024-02-13 Adjusted Motor Rack B to avoid sanding
    Change made to Motor Rack B at interface point to Motor Rack A to avoid sanding after 3D printing.
    SolidWorks design files:
    Noora's "Prototype 10/Motor Roack B 10/ Motor Rack B 10_2.SLDPRT"
    [Motor Rack B 10_2.STL, Motor Rack B 9 .STL]
2024-02-14 Added MD assembly guide
2024-02-15 Added MD Assembly Manual
    Copied the MD Assembly manual so we don't use a PDF anymore
